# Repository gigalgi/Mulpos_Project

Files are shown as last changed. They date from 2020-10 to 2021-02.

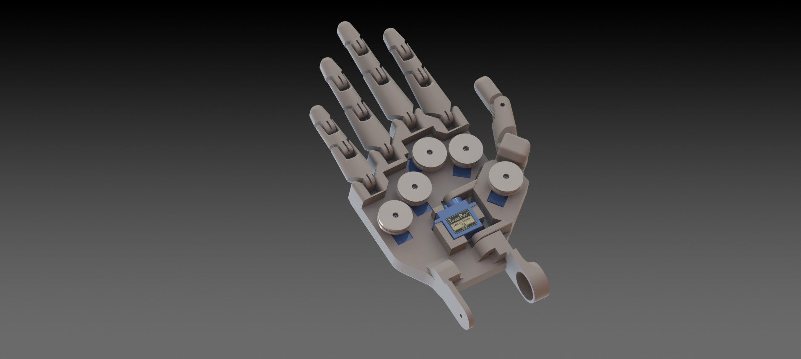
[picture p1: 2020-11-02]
MULPOS Piezas/Render/9.JPG

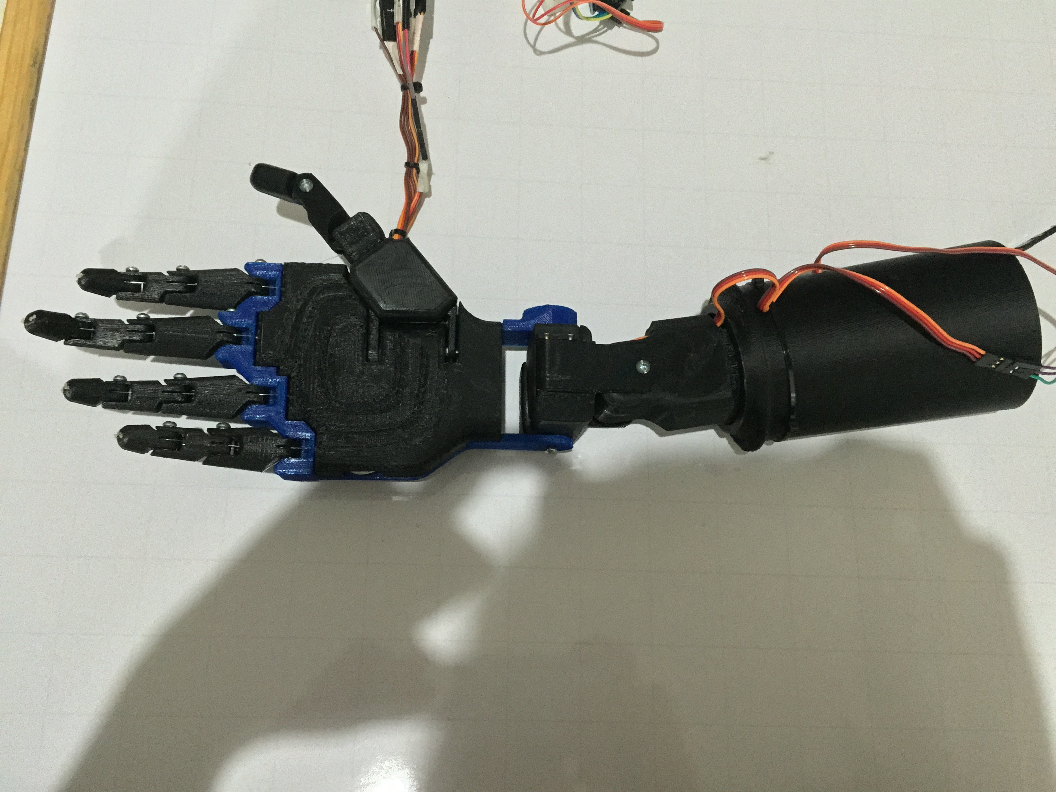
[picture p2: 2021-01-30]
STARPI/Render/IMG_1585.JPG

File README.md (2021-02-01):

# MULPOS Project

El objetivo del proyecto MULPOS es el diseño y desarrollo de sistemas protésicos caracterizados principalmente 
por su bajo costo y por su arquitectura open source, además de ofrecer alternativas funcionales a las prótesis 
tradicionales.

Para la reducción de costos de los sistemas a diseñar se proponen técnicas aditivas de construcción 
como la impresión 3D. La experiencia de controlar un miembro artificial de una manera intuitiva y similar a la de 
uno natural es prerrequisito del proyecto, por lo que se busca desarrollar interfaces basadas en bioseñales como 
son las que pueden ser obtenidas a través de los músculos o el cerebro.

Se busca a través de la reducción de costos permitir a la mayor parte de la población la mejora de la calidad de vida
con prótesis que emulen el miembro ausente tanto en aspectos de apariencia como funcionales.
El caracter open source del proyecto tiene como objetivo el facilitar la construcción de estos dispositivospor personas 
con conocimientos limitados de diseño CAD además de fomentar el interés por el desarrollo de destrezas en esta área.   

Para mas informacion visite nuestro sitio web www.moveorobotics.com o contactenos a traves de email: support@moveorobotics.com

##

The objective of the MULPOS project is the design and development of prosthetic systems characterized mainly by 
their low cost and open source architecture, in addition to offering functional alternatives to traditional prostheses.

To reduce the costs of the systems to be designed, additive construction techniques such as 3D printing are proposed. 
The experience of controlling an artificial limb in an intuitive way and similar to that of a natural one is a prerequisite
of the project, which is why it seeks to develop interfaces based on biosignals such as those that can be obtained through 
the muscles or the brain.
       
It is sought through cost reduction to allow the majority of the population to improve the quality of life
with prostheses that emulate the absent limb in both appearance and functional aspects.The open source 
nature of the project aims to facilitate the construction of these devices by people with limited knowledge
of CAD design, as well as to encourage interest in the development of skills in this area.

For more information visit our website www.moveorobotics.com or contact us via email: support@moveorobotics.com

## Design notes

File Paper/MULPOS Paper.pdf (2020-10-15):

# Diseño de una prótesis mioeléctrica de miembro superior de código abierto

Galvis Giraldo Gilberto

1

, García Arias Luis Felipe²

, Jaramillo Pineda Victor Alfonso³ gigalgi@hotmail.com¹

, feligar14@hotmail.com²

, victor.jaramillo@ucaldas.edu.co³ Department of Physics, Mechatronics Engineering Program, University of Caldas Manizales (Colombia)

Resumen__El propósito de este artículo fue desarrollar una prótesis capaz de emular la naturaleza y funcionamiento de una mano humana, de tal manera que el individuo que la use logre mejorar su calidad de vida sin tener que someterse a métodos invasivos que requieren otros tipos de procedimientos. La adquisición de las señales eléctricas que activan el movimiento de los músculos se logró por medio de un sistema de electromiografía superficial (ECG), con esto se identificaron los patrones de las señales obtenidas indicando las diferentes funciones de la mano y se tradujeron en movimientos mecánicos por medio de ocho servomotores integrados en el diseño de la prótesis. Para captar las señales eléctricas se implementó un electromiógrafo con cinco electrodos, para el procesamiento de la señales y la ejecución de los movimientos se optó por un microcontrolador Arduino, el diseño se realizó en un software de dibujo asistido por computadora (CAD) y finalmente aprovechando la tecnología de impresión 3d se puedo obtener el modelo físico de la prótesis teniendo como valor agregado su bajo puesto que el objetivo es que sea asequible para cualquier persona. Finalmente se logró un control eficiente y versátil similar a como se controla la mano del ser humano, para el bien y mejoramiento de la calidad de vida de las personas que no cuentan con grandes recursos económicos y carecen de esta extremidad.

Palabras claves: Arduino, bajo costo, código abierto electromiografía, electrodos, prótesis, servomotores, señales,

Abstract__ The purpose of this article was to develop a prosthesis capable of emulating the nature and functioning of a human hand, so that the individual who achieves use improve their quality of life without having to undergo invasive methods that require other types of procedures, the acquisition of the electrical signals that trigger muscle movement is achieved through electromyography (ECG) by placing electrodes on the skin, with patterns that the signals obtained were identified indicating the different functions of the hand translating into mechanical movements through integrated in the design of the prosthesis servomotors, a total of 8 servo motors is used to capture the electrical signals one electromyograph five electrodes was implemented, for the processing of signals and execution of movements chose a Arduino microcontroller, the design is performed in a software-aided drafting (CAD) and finally taking advantage of 3D printing technology will I get the physical model of the prosthesis having as value added his low since the goal is to make it affordable for Anyone. Finally an efficient and versatile control similar to the human hand, for good and improving the quality of life of people who do not have large financial resources and lack of this tip is controlled achieved.

Keyword: Arduino, low cost, open source, electromyography, electrodes, prosthesis, servomotors, signals

I. Introducción

La tendencia global hacia el uso de dispositivos wereables desafía al desarrollo de productos compactos y fáciles de usar, el diseño de las interfaces entre estos y el usuario constituye la parte clave del proceso. Así mismo, se presenta una tendencia en investigadores hacia el desarrollo de dispositivos e interfaces orientadas a usuarios que poseen algún tipo de limitación física o motora. Como ejemplos se puede encontrar en la literatura científica desarrollos que se basan en el reconocimiento del usuario como parte integral del sistema a través de técnicas de procesamiento de imágenes [2,7], otros enfoques se basan en la adquisición de bioseñales como son las obtenidas a través de dispositivos de electroencefalografía (EEG), electrooculografía (EOG) y electromiografía (EMG) [3, 4, 5, 6].

Entre los desarrollos mencionados se encuentran dispositivos protésicos que permitan a usuarios con algún grado de amputación, la realización de todo tipo de tareas de la manera más fiel posible a la que le permitiría una extremidad natural. Entre las características destacables de una buena prótesis de mano se encuentran: Versatilidad en la ejecución de gestos, integridad con el tiempo de la interfaz implementada, bajo costo, apariencia realista. Aunque existen en el mercado alternativas de vanguardia que posibilitan un amplio reconocimiento de gestos, constituyen opciones de alto costo, lo que imposibilita el acceso de una amplia gama de la población.

En este trabajo se propone el diseño de una prótesis de mano de código abierto, que pueda ser implementada a través de métodos aditivos de fabricación. Se busca obtener un dispositivo de bajo costo que pueda ser personalizado por un usuario con conocimientos básicos de CAD. Del mismo modo se propone un sistema de adquisición y procesamiento de señales EMG basado en una plataforma de código abierto.

II. | Marco Teórico

En la actualidad existen diferentes tipos de prótesis (ver tabla 1), algunas difíciles de utilizar, baja eficiencia y algunas demasiado costosas y de difícil acceso para la mayoría de las personas. Se pueden encontrar prótesis de miembro superior del tipo protésico, que solo realizan presión tridigital con oposición entre los dedos índice y medio con el pulgar, este tipo de prótesis pueden ser mecánicas o electromecánicas, son relativamente económicas y de fácil acceso. Existen también sistemas protésicos de tipo de gancho que realizan presión digital, ofreciendo funcionalidad limitada al usuario.

Tipo | Características Principales
Mecánica | Se usa con la función de cierre o apertura a voluntad. Solo puede ser utilizada para el agarre de objetos relativamente grandes y redondos, debido a la poca precisión del mecanismo.
Eléctrica | Utiliza motores eléctricos en los dispositivos terminales, muñeca y codo, con una batería recargable. Es posible controlarla de varias formas: servo control, botón pulsador o un interruptor con arnés.
Híbrida | Combina el movimiento del cuerpo con el accionamiento por electricidad. Este concepto es utilizado en la prótesis transhumerales, donde el codo es accionado por el cuerpo y el dispositivo terminal (gancho o mano) es de accionamiento mioeléctrico.

Tabla 1. Fuente: http://www.elhospital.com/temas/Colombia-avanza-en-el-desarrollo-de-protesis-mioelectricas+102438, consultada el día 28 de julio de 2015

La tecnología mioléctrica comenzó a implementarse en las prótesis de extremidad superior de tipo protésico a mediados del siglo XX [7]. La incorporación de sensores que captan la actividad electromiográfica (EMG) de los músculos remanentes del muñón y lo traducen en un movimiento de la mano protésica constituyo un gran salto en la calidad de las prótesis de extremidad superior [8]. Las manos mioeléctricas, los usuarios a menudo abandonan la prótesis mioeléctricas de antebrazo debido a los problemas de control y la ausencia de retroalimentación. Muchas de las investigaciones modernas se centran en el aumento de la funcionalidad de las nuevas prótesis, pero existen otro tipo de trabajos donde los más importante es la aceptación del usuario [9] y la adaptabilidad del usuario con la prótesis buscando así construir una prótesis que tenga gran similitud con la calidad de los movimientos a la de una mano humana.

Por otro lado existen desarrollos de prótesis de miembro superior cada vez más versátiles, que incorporan tecnología de vanguardia, como lo es el sistema creado por Touch Bionics llamado iLimb Ultra. La prótesis se ve y se mueve como una mano natural, tiene todos los dedos motorizados permitiendo emular movimientos naturales y además el usuario puede personalizarla para sus necesidades específicas [10]. Se presenta como un dispositivo funcional pero de difícil acceso con un costo que oscila alrededor de 100.000 dólares.

En nuestro trabajo proponemos una prótesis de miembro superior funcional, con movimientos independientes en cada uno de los dedos y que su costo de fabricación no supere los 150 dólares para permitir el acceso de cualquier usuario al dispositivo. Se propone la impresión 3D como forma de fabricación puesto que permite producir prototipos personalizados y resulta la mejor opción para construir una prótesis de bajo costo para personas de bajos recursos [11].

III. | Métodos y materiales

Para la construcción de la prótesis que se propone en este trabajo se tuvo en cuenta diferentes parámetros de diseño, entre ellos la adaptabilidad para el futuro usuario, el control electrónico y la eficiencia, todo teniendo que cuenta que debe ser una prótesis que se asemeje en sus movimientos a los de la mano humana, fácil de controlar y que su costo de fabricación sea inferior a 150 dólares. A continuación se detallan cada una de las etapas de diseño y construcción.

A. Estructura física de la mano y parámetros de diseño

El diseño y control de esta prótesis se basa en las características mecánicas, eléctricas y morfológicas de la mano, la muñeca y el antebrazo del ser humano. Se busca imitar características de apariencia y funcionalidades perfeccionadas durante miles de años de evolución.

Para el diseño de esta prótesis de mimbro superior se usó un software de diseño asistido por computadora (CAD), el cual permite realizar pruebas de resistencia y esfuerzo al igual que realizar múltiples modificaciones sin la necesidad de fabricar prototipos. En el diseño se consideraron tanto el aspecto físico como el funcionamiento mecánico, plasmando en el diseño un esqueleto que forma la estructura base. Esta estructura integra el tejido y los huesos ubicados en la palma y dorso de la mano, además de fusionar los múltiples huesos que componen la muñeca humana (ver figura 1). Se conservan las falanges proximal, media y distal como elementos independientes, unidas en la mano humana a través de articulaciones metacarpofalángicas e interfalángicas. Las articulaciones metacarpofalángicas son articulaciones condíleas que permiten: flexión, extensión, abducción, aducción, circunducción y una rotación limitada [12]. Las articulaciones interfalángicas de la mano son de tipo bisagra y permiten principalmente los movimientos de flexión y de extensión [12]. La ubicación de estas articulaciones se muestra en la figura 2.

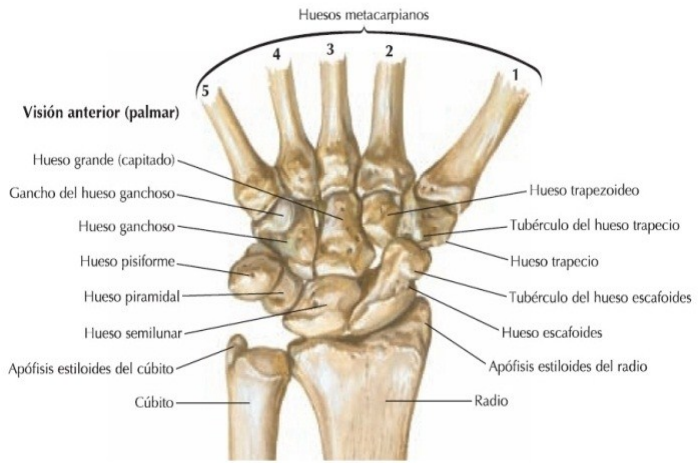
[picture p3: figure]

Figura 1.Huesos que componen la muñeca humana. Imagen tomada de Atlas de Anatomía Humana - Netter - 5ed p 440

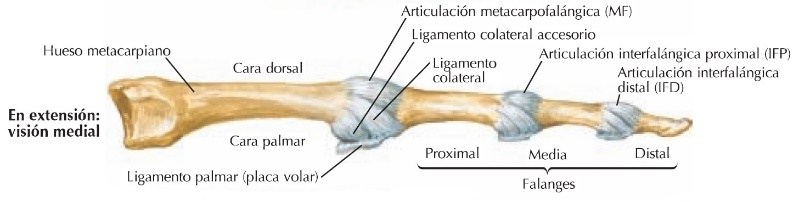
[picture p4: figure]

Figura 2. Ubicación de las articulaciones de un dedo de la mano humana

El material seleccionado para construir el prototipo fue el plástico ABS dada su resistencia, bajo peso y flexibilidad características que comparte con los huesos humanos, este material tiene como valor su bajo costo, maleabilidad y resistencia. Las articulaciones fueron incluidas en el diseño igualando su funcionamiento al acoplar las falanges como eslabones que rotan alrededor de un eje. Para lograr los movimientos mencionados de los dedos se emulo con servomotores el conjunto de músculos: flexor profundo y extensor de los dedos, que se encuentran en el antebrazo. El músculo flexor profundo produce el movimiento cuatro tendones que pasan por el túnel del carpo y se dirigen hacia los cuatro dedos mediales. Los tendones cruzan la muñeca, por lo que también puede flexionar dicha articulación [12]. El músculo extensor de los dedos es extensor de los cuatro dedos mediales (índice, medio, anular y meñique), cada tendón se inserta en la base de las superficies dorsales de las falanges media y distal [12].

Existe también otro musculo que es el flexor largo del pulgar que origina el movimiento a un único tendón alargado, pasa por el túnel del carpo, y hace que se flexione el pulgar [13]. Otro musculo que interfiere es el músculo extensor largo del pulgar, que extiende todas las articulaciones de este [12]. (Ver figura 3), también se tuvo en cuenta el musculo oponente del pulgar que rota y flexiona el primer metacarpiano sobre el trapecio, de manera que sitúa la yema del pulgar enfrentada a las de los otros dedos [12]. (Ver figura 4).

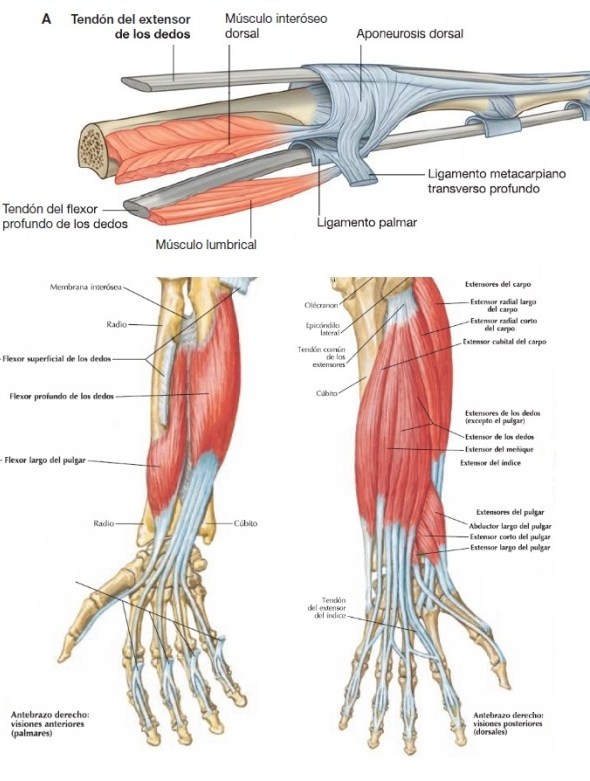
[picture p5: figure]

Figura 3. Musculo extensor largo del pulgar. Imagen tomada de Atlas de Anatomía Humana - Netter - 5ed. pp 429,431

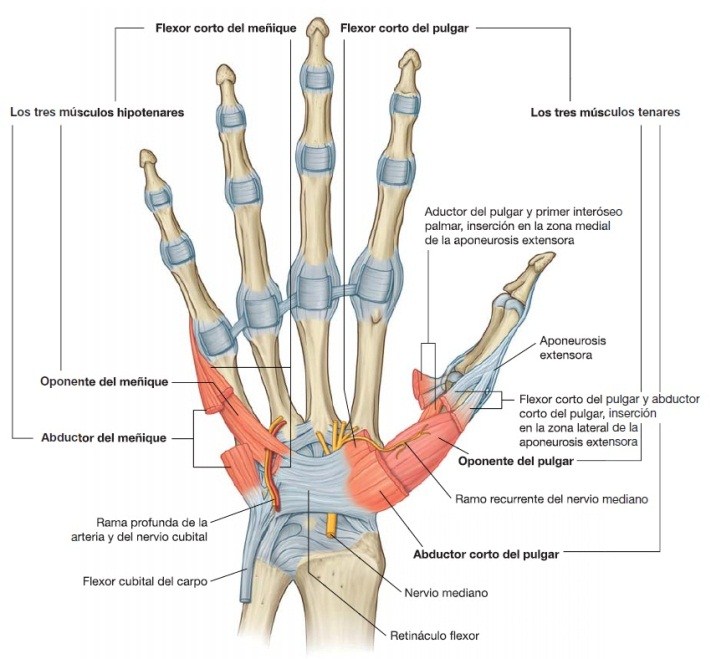
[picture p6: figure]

Figura 4. Mano humana con los músculos flexores. Imagen tomada de Gray anatomía para estudiantes 2ª ed. pag 765

El movimiento muscular mencionado se activa por neuronas motoras asociadas a cada músculo. Estas células nerviosas son comandadas a través de señales eléctricas que se originan en el cerebro y viajan a través de la médula espinal. Para determinar la posición en que se encuentra cada una de las partes del cuerpo se encuentra una estructura llamada huso neuromuscular que está conformado por neuronas sensitivas y motoras (Ver figura 5). Este tipo de estructuras se encuentra en las regiones tendinosas de los músculos y es más abundante en las regiones que deben ejecutar movimientos con destreza. [14]

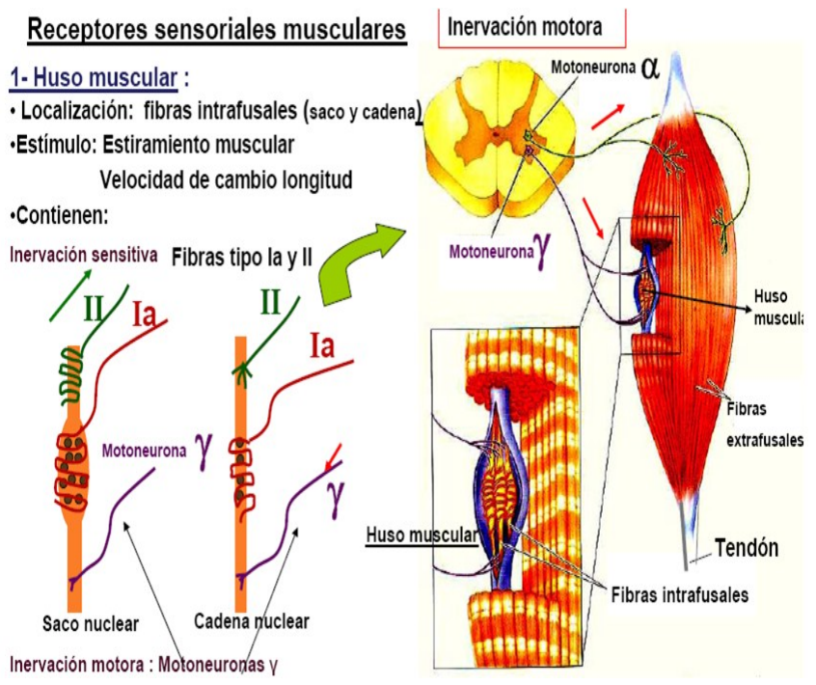
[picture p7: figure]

Figura 5. Huso muscular.
Imagen tomada de http://1.bp.blogspot.com

Para los tendones se seleccionó como material el nylon debido a su resistencia a la extensión y capacidad de flexionarse sin sufrir fatiga, las funciones de contracción y relajación de los músculos se producen con servomotores debido a su fácil manejo, gran cantidad de fuerza y tamaño reducido, siendo ideales para ser incorporados dentro de la estructura de la mano (ver figura 5), permitido realizar de manera muy precisa el cierre y apertura de la mano ya que se cuenta con un total de seis servomotores de los cuales dos de ellos son usados por el pulgar, uno para realizar la flexión y extensión del pulgar y el otro para realizar el movimiento de oposición del pulgar los cuatro servos restantes se dividen para los otro cuatro dedos, esto con el fin de otorgarle a la prótesis la misma libertar de apertura y cierre individual o conjunta de los de dedos para una mejor sujeción de los objetos, también se agregaron los movientes de la muñeca y el antebrazo que son los movimientos de pronación, supinación, flexión y extensión de la muñeca, para estos movimientos se involucran otros músculos [12] (ver figura 6).

Para reemplazar el papel de los tendones se seleccionó el Nylon debido a su capacidad de flexionarse y estirarse sin sufrir fatiga.
[22] Se seleccionan servomotores para realizar las funciones de contracción y relajación de los tendones, ejecutadas en el cuerpo por los músculos. Como criterio de diseño para la selección de los actuadores mencionados se establecieron características como el tamaño, torque y facilidad al momento de ser controlados. El Nylon se sujeta de la falange distal y pasa por las falanges media y proximal sobre las caras anterior y posterior de cada uno de los dedos formando dos tendones en cada uno. El material usado para reemplazar los tendones se conecta al actuador a través de una polea, cada una de las direcciones de giro del motor corresponde a una acción de contracción o relajación del músculo que a su vez se relaciona con la flexión o extensión del dedo. (Figura 7)

El sistema de movimiento de los componentes de la prótesis se compone de seis actuadores. Cada dedo posee un servomotor que permite los movimientos de flexión y extensión individual y en conjunto el cierre y apertura precisa de la prótesis. Se añade un actuador adicional en el dedo pulgar que le añade un movimiento de oposición y mejora la sujeción de objetos. Se agregó al sistema un mecanismo de 4 grados de libertad (DOF) a través de tres servomotores que permite los movimientos de pronación, supinación, flexión y extensión de la muñeca, desviación cubital y desviación radial (aducción y abducción).

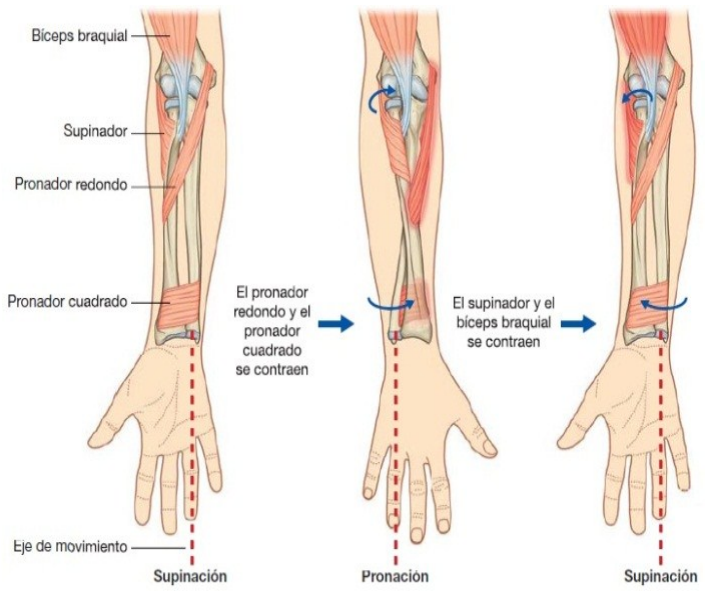
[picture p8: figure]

Figura 6. Músculos de supinación y pronación.
Imagen tomada de Gray anatomía para estudiantes 2ª ed. pag 736

El flexor cubital del carpo es el más medial de los músculos flexores del plano superficial, su función es la de flexionar y aducir la articulación de la muñeca, el músculo flexor radial del carpo se sitúa lateral al palmar largo, y tiene un tendón largo y prominente en la mitad distal del antebrazo [15]. El flexor radial del carpo es un potente flexor de la muñeca, y también puede abducir esta articulación (ver figura 6), El músculo extensor radial largo del carpo se origina en la zona distal de la cresta supracondílea y en el epicóndilo lateral del húmero el extensor radial largo del carpo extiende y abduce la muñeca, el músculo extensor cubital del carpo se sitúa medial al extensor del dedo meñique. Tiene su origen en el epicóndilo lateral, y su tendón se inserta en la cara medial de la base de V metacarpiano.

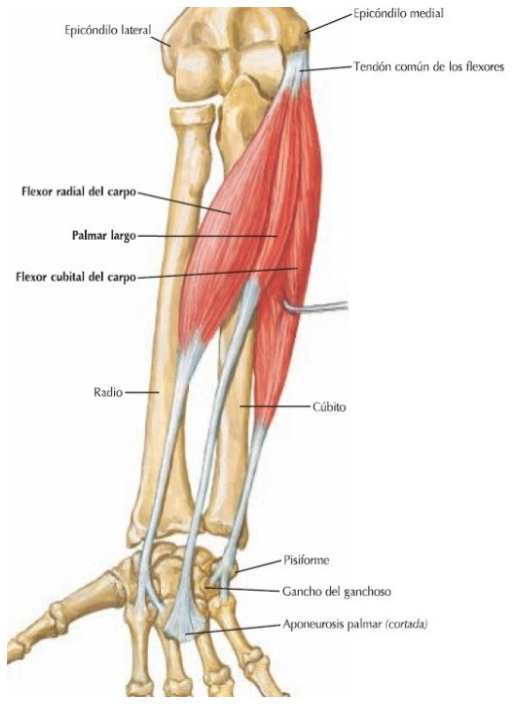
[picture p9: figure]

Figura 7. Músculo flexor radial del carpo, flexor cubital del carpo y palmar largo.
Imagen tomada de Atlas de Anatomía Humana - Netter – 5ª ed. pag 430

El extensor cubital del carpo extiende y aduce la muñeca [12] (ver figura 8), estos movimientos son implementados en el diseño mediante una unión con la muñeca utilizando un mecanismo que simula una junta universal por medio de dos servos con los cuales se logran los movimientos de flexión de la muñeca, extensión de la muñeca, desviación cubital y desviación radial (abducción y aducción), los movimientos de pronación y supinación se realizan con un último servo el cual al girar hacia un lado o hacia el otro imitando de igual manera que el mecanismo del cardan de forma muy precisa dichos movimientos utilizan así un total de 9 servo motores para lograr emulara con gran exactitud los movimientos más importantes de la mano humana.

Para el control de dicha prótesis se captan las señales eléctricas que activan el movimiento de los músculos, por medio de una electromiografía (EMG) colocando electrodos sobre la piel se identificaron patrones en la señales obtenidas que indicaran movimientos como la flexión, extensión, supinación, pronación, desviación cubital y desviación radial traduciéndolas en movimientos mecanismos por medio de los servos ya mencionados integrados en la prótesis asemejándose al sistema nerviosos pues el servo motor emula de igual manera las partes básicas empleadas para realizar el movimiento siendo su motor el musculo, su controlador las neuronas motoras y los huesos neuromusculares siendo quienes ejecutan la información recibida y envía nueva información sobre su longitud es decir que tan contraído esta y su posición. Para procesar estas señales se usó un microcontrolador Arduino siendo este quien da la orden final de que movimiento se debe realizar de igual manera que lo hace el cerebro al enviar la información en forma de pulsos eléctricos a través del sistema nervioso llegando a las neuronas motoras y huesos neuromusculares dispuestos en los músculos indicándole la instrucción que debe ejecutar el musculo realizando así el movimiento y tarea deseada.

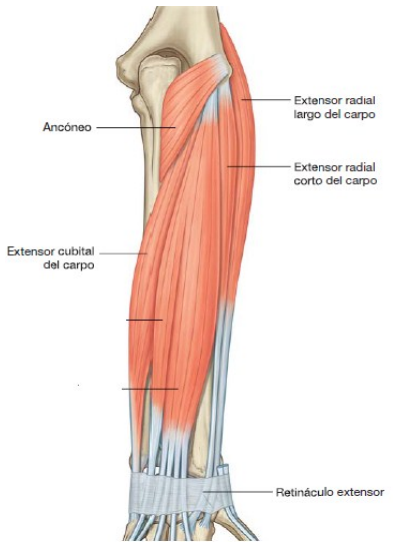
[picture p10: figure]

Figura 8.Músculo extensor cubital del carpo.
Imagen tomada de Gray anatomía para estudiantes 2ª ed. pag 746

Después del análisis anatómico de la mano humana que se realizó se procedió a diseñar un prototipo teniendo en cuenta todos los parámetros de movimiento (ver figura 9).

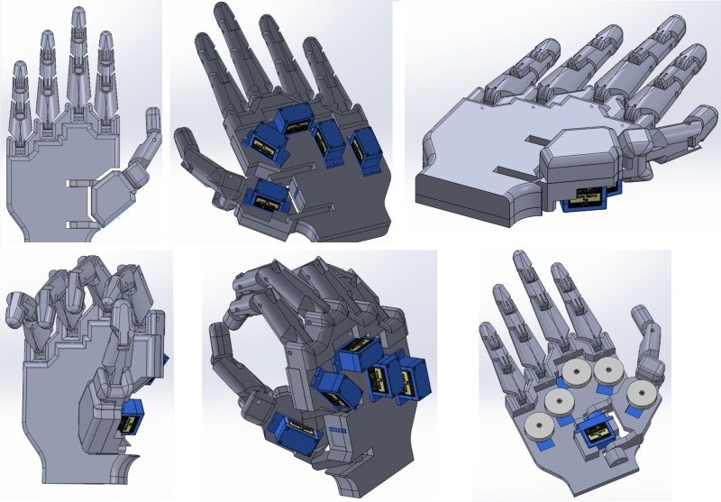
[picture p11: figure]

Figura 9. Diseño final de la prótesis de miembro superior.

B. Adquisición de señales EMG

Desde mediados del siglo 20 se ha abordado el uso de señales tomadas directamente desde los músculos como una manera de controlar diferentes tipos de dispositivos [16]. Esta tendencia ha aumentado recientemente a medida que mejoran los métodos de fabricación aditiva y las técnicas de adquisición y procesamiento
de | bioseñales. | La | posibilidad | de | obtener | señales
electromiográficas (EMG) desde la superficie de la piel de un miembro amputado se presenta como una forma intuitiva en la que el usuario puede comandar prótesis activando las unidades motoras residuales del miembro objetivo [17,18]. Para el control intuitivo de una prótesis como la que se presenta en este estudio se presentan a continuación consideraciones en el diseño de un sistema de adquisición de señales EMG y en el modo con que estas son procesadas.

Sistema de Electromiografía

En la figura se muestra el diagrama de bloques de un sistema para la adquisición de señales EMG. El sistema se compone de una etapa de adquisición y pre amplificación de la señal, una etapa de filtrado y amplificación posterior. Para el dispositivo a desarrollar se incluye en el esquema una etapa de acondicionamiento que permita ajustar los valores de tensión de la señal para que esta pueda ser procesada por un microcontrolador. La amplitud de la bioseñal objetivo ronda los 10 mV [19], por lo que se selecciona una ganancia del sistema de 1200. Se establece una ganancia de 40 para la etapa de preamplificación y una de 30 para la etapa de amplificación. La etapa de filtrado se compone por un filtro pasa altas y uno pasa bajas, cuyas frecuencias de corte se establecen en 70 Hz para el filtro pasa altas y 500 Hz para el filtro pasa bajas, típicamente esta primera se establece entre los 10 y los 20 Hz. Las frecuencias más bajas en el espectro de la señal corresponden a los mecanismos de disparo de los músculos motores y no contribuyen significativamente al sistema de reconocimiento de gestos [20,21]. De este modo Li et al [21] establecen en su investigación una frecuencia de corte de 60 Hz para mejorar el rechazo del sistema a señales características de la red eléctrica europea (50 Hz) y así mismo se selecciona una frecuencia de corte de 70 Hz para el dispositivo desarrollado en este trabajo por el entorno en que será usado

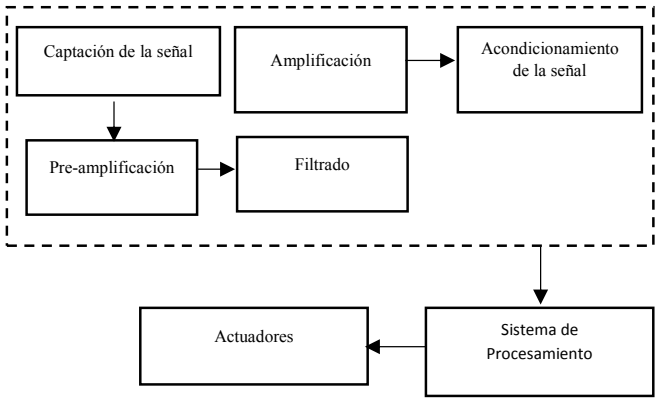
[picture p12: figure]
Captación de la señal; Pre-amplificación; Filtrado; Amplificación; Acondicionamiento; de la señal; Sistema de Procesamiento; Actuadores

Diagrama de bloques del sistema de adquisición y posicionamiento.

Se diseñó un circuito electrónico para el electromiógrafo con un amplificador de instrumentación de referencia INA126, debido a las características de rechazo de modo común, bajo voltaje de offset y a su bajo costo, en la figura 10 se muestra el diagrama del circuito.

IV. Resultados

Primero se diseñó y se construyó un prototipo en madera (ver figura 11) que funcionaba con comandos de voz y con una aplicación para dispositivo móvil [23], utilizando los sensores del teléfono (acelerómetro y giroscopio) este prototipo inicial sirvió para analizar los movimientos, obtener datos de diseño y de eficiencia, ya con todos los datos necesarios se procedió a diseñar una prótesis más eficiente como la que se mostró en este trabajo.

En el primer prototipo de la prótesis la forma de oposición de pulgar se realizaba de manera que el pulgar rotara sobre sí mismo, manteniendo su posición con respecto a la palma, pero variando su dirección rotando desde una posición en la que se mantenía paralelo a los demás dedos hasta una posición en la que el pulgar podía flexionarse hacia adentro de la palma realizando la oposición, pero dado que el pulgar se mantenía en el mismo lugar al rotar le impedía a la prótesis una buena sujeción, por estos motivos se decido modificar este sistema de forma que el pulgar se opone para mejorar el agarre al sujetar cualquier tipo de objeto esta nueva forma hace rotar el dedo hacia la palma de la misma manera en la que se opone el pulgar de la mano del humano realizando un movimiento más natural acorde con la bilogía humana, otorgando mayor funcionalidad, además este nuevo prototipo puede tocar todos los dedos desde la punta hasta la base proporcionando una mejor eficiencia para la sujeción de objetos pequeños.

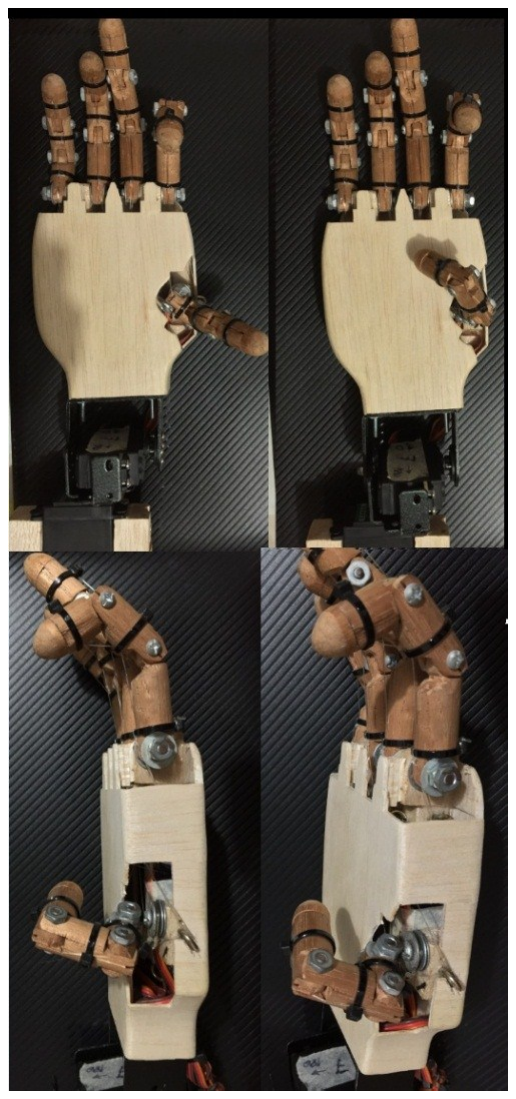
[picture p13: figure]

Figura 11. Diseño inicial en madera de la prótesis.

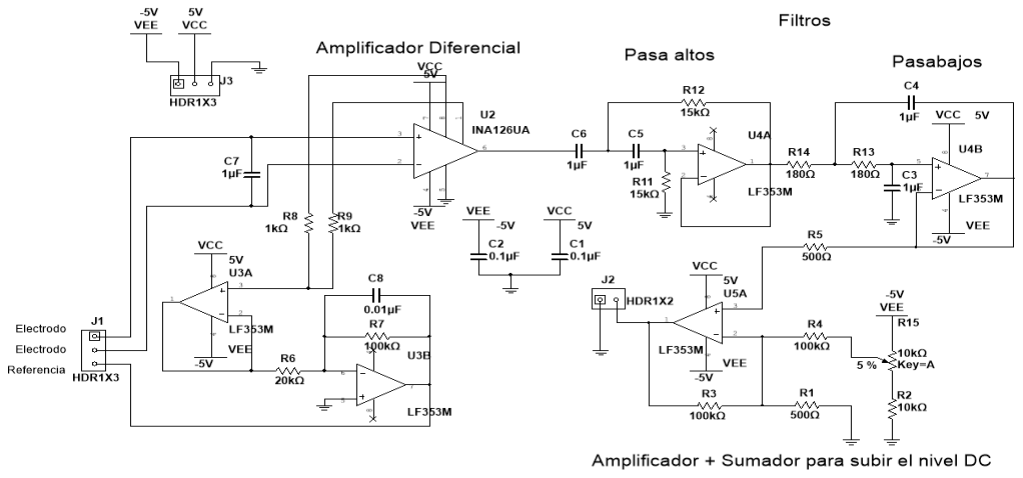
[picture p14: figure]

Figura 10. Diagrama esquemático del electromiógrafo.

V. Conclusiones

Se obtuvo una prótesis de miembro superior con un costo de fabricación inferior a los 150 dólares lo que hace que sea accesible para casi cualquier persona que tenga ausencia de un miembro superior.

Cambiando el diseño mecánico del dedo pulgar se obtiene un aumento considerable de la funcionalidad de la prótesis, lo que se pudo verificar comparando las dos prótesis construidas.

REFERENCIAS

[1] M. Al-Rousan, K. Assaleh, A wavelet- and neural network-based voice systemfor a smart wheelchair control, J. Frankl. Inst.-Eng. Appl. Math. 348 (1) (2011)90–100,
[2] X. Shen, G Hua, L. Williams, Y. Wu, Dynamic hand gesture recognition: An exemplar-based approach from motiondivergence fields, Image and Vision Computing 30 (2012) 227–235.
[3] D. Purwanto, R. Mardiyanto, K. Arai, Electric wheelchair
control | with gazedirection | and | eye | blinking, | in:
Proceedings of the 14th International Sympo-sium on Artificial Life and Robotics, AROB, Oita, Japan, February 5–7, 2009,pp. 400–436
[4] J.Y. Long, Y. Li, H. Wang, T. Yu, J. Pan, F. Li, A hybrid brain com-puter interface to control the direction and speed of a simulated or realwheelchair, IEEE Trans. Neural Syst. Rehabil. Eng. 20 (5) (2012) 720–729
[5] R. Barea, L. Boquete, M. Mazo, E. Lopez, L.M. Bergasa, EOG guidance of awheelchair using neural networks, in: 15th International Conference onPattern Recognition, ICPR, vol. 4, Barcelona, Spain, 2000, pp. 668–671,
[6] A. Phinyomark, C. Limsakul, A review of control methods for elec-tric power wheelchairs based on electromyography signals with specialemphasis on pattern recognition, IETE Tech. Rev. 28 (4) (2011) 316–326.
[7] Zecca M., Micera S., Carroza M., Dario P., “Control Of Multifunctional Prosthetic Hands By Processing The
Electromyographic | Signal”, | Critical | Reviews™ | in
Biomedical Engineering. Vol. 30, pp. 459 485.2002.
[8] Garcia, D., Espinoza, M., J., «Avances en prótesis: una mirada al presente y al futuro,» Revista Médica Clínica Las Condes, vol. 25, nº 2, pp. 281-285, 2014.
[9] T. Bionics, «Touch Bionics,» 2015. [En línea]. Available: http://www.touchbionics.com/products/active-prostheses/ilimb-ultra. [Último acceso: 21 07 2015].
[10] B. Peerderman, «Myoelectric forearm prostheses: State of the art from a user-centered perspective,» Journal of rehabilitation research and development, vol. 48, nº 6, pp. 719-738, 2011.
[11] Loera Perez., E., A., «Proyecto E-Nable Sobre El Desarrollo De Prótesis Mecánicas,» Universidad Autonama de Nuevo Leon.
[12] Richard L. Drake, A. Wayne Vogl, Adam W. Mitchell. Anatomía para estudiantes, Barcelona: Elsevier, 2010.
[13] Schunke, | Shulte, | Shumacher, | Voll, | Wesker.,
PROMETHEUS Texto y Atlas de Anatomía, Panaericana, 2005.
[14] John a. Kiernan, lippincott., W., wilkins.,W., Kluwer., H., El sistema nervioso humano: Una perspectiva anatómica, Barcelona: Lippincott Williams and Wilkins. Wolters Kluwer Health, 2009.
[15] Zecca M., Micera S., Carroza M., Dario P, «Control Of Multifunctional Prosthetic Hands By Processing The
Electromyographic | Signal,» | Critical | Reviews™ | in
Biomedical Engineering, vol. 30, pp. 459-485, 2002.
[16] Ajiboye. A. B., Weir. R. F., «A heuristic fuzzy logic approach to EMG pattern recog-nition for multifunctional prosthesis control,» IEEE Trans. Neural Syst. Rehabil.Eng, vol. 13, nº 3, p. 280–291, 2005.
[17] F.V.G. Tenore, A. Ramos, A. Fahmy, S. Acharya, R. etienne-Cummings,N.V. Thakor, «Decoding of individuated finger movements using surfaceelectromyography,» IEEE Trans. Biomed. Eng, vol. 56, nº 5, p. 1427–1434, 2009.
[18] L.J. Hargrove, G. Li, K. Englehart, B. Hudgins, «Principal
components | analysispreprocessing | for | improved
classification | accuracies | in | pattern-recognition-based
myoelectric control,» IEEE Trans. Biomed. Eng, vol. 56, nº 5, p. 1407–1414, 2009.
[19] Maria Hakonena, Harri Piitulainenb, Arto Visalaa, «Current state of digital signal processing in myoelectric interfaces and related applications,» Biomedical Signal Processing and Control, pp. 334-359, 2015.
[20] D.F. Stegeman, H.J. Hermens, «Standards for surface electromyography,» in:The European Project Surface EMG for Non-Invasive Assessment of Muscles(SENIAM), 2007.
[21] G. Li, Y. Li, L. Yu, Y. Geng, « Conditioning and sampling issues of EMG signals in motion recognition of multifunctional myoelectric prostheses,» Ann. Biomed. Eng, vol. 39, nº 6, p. 1779–1787, 2011.
[22] A. Carrera, «Elasticidad y dureza de los huesos», Universidad Tecnológica de Equinoccial, Escuela de Odontologia, 2013.

[23] Jaramillo Pineda, V. A., Pineda, J., & Garcia Arias, L.F., «Design of an automatic voice controlled system and remote control», IEEE Explora, pp. 1-5, 2014.

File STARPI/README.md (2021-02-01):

# STARPI

El proyecto STARPI nace a partir del proyecto MULPOS y el aprovechamiento de sus características para solucionar problemas en otros sectores en los que es necesario la presencia de la mano humana en algunas aplicaciones de alto riesgo, por este mismo motivo es aun mas riesgoso exponer una vida humana a algunas de estas actividades como: inspección en plantas radioactivas, inspección en lugares de presencia de gases (tóxicos o inflamables), inspección de expertos en aplicaciones especificas, control en desminado y desarmado de bombas.

Estas aplicaciones tienen algo en común, ya se evidencian antecedentes de robots de inspección o manipulación,muchos de estos con pinzas para sujeción o transporte de elementos la idea principal del proyecto es aprovechar estos robot para hacer un híbrido entre la mano humana y los robots como elementos de transporte y virtualización. Se emplean diferentes tecnologías para monitoreo y manipulación utilizando la visión artificial como control del STARPI.

Para mas informacion visite nuestro sitio web www.moveorobotics.com o contactenos a traves de email: support@moveorobotics.com

##

The STARPI project was born from the MULPOS project and the use of its characteristics to solve problems in other sectors in which the presence of the human hand is necessary in some high-risk applications, for this same reason it is even more risky to expose human lifes to some of these activities such as: inspection in radioactive plants, inspection in places of presence of gases (toxic or flammable), inspection of experts in specific applications, control in demining and dismantling of bombs.

These applications have something in common, there is already evidence of a history of inspection or handling robots, many of these with clamps for holding or transporting elements.The main idea of the project is to take advantage of these robots to make a hybrid between the human hand and robots such as elements of transport and virtualization. Different technologies are used for monitoring and manipulation using mainly artificial vision to control STARPI. 

For more information visit our website www.moveorobotics.com or contact us via email: support@moveorobotics.com

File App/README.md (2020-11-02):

# app android para el control de MULPOS
* Aqui encontraras el .apk para instalar el app de control para MULPOS si desea puedes modificarla el proyceto fue desarrollado con appinveror2.
Junto al apk esta el .aia que puede abrir y editar en la plataforma appinventor2 y construir una nueva app.
* http://ai2.appinventor.mit.edu/
##
Para mas informacion visite nuestro sitio web www.moveorobotics.com o contactenos a traves email: support@moveorobotics.com

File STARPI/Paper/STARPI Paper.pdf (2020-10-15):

Abstract— the world of robotics is becoming wider day, we can see how from decades ago robots provide aid and reduce risks to humans, based on mixed reality and the anatomy of the human hand a robotic hand that simulates create a lot of human movements. Also the system fully complies with the goals establecidad presenting a smooth functioning of artificial vision systems and mechanical design of the hand.

Index Terms— PID, Opencv, control system, real time, vision system, mixed reality, HSV filter.

I. INTRODUCCIÓN
L uso de la robótica en situaciones de operaciones precisas y manipulación de objetos a distancia, es cada vez más frecuente, y nos permite disminuir la intervención humana directa para evitar accidentes. De otro lado, vemos como el internet nos es cada vez más útil en el logro de la integración, visualización y manipulación remota de objetos, archivos e imágenes, con lo que se mejora también en el caso de la robótica, el control y el análisis de las operaciones. Considerando que en la actualidad los robots de inspección y manipulación de objetos en actividades remotas, tienen como manipulador principal una pinza con movilidad limitada, se ha desarrollado un proyecto que busca remplazar esta pinza por una mano con movimientos complejos similares a los obtenidos por la mano humana.
El proyecto consta de un sistema de realidad mixta [25], el cual genera mayor inmersión del operador, permitiéndole más comodidad al momento de manipular objetos y sentir profundidad por medio de esta; su principal innovación es la mano capaz de manipular una mayor cantidad de objetos y de realizar movimientos más complejos [30] que la pinza. La mano consta de movimiento independiente en cada uno de los cinco dedos, puede realizar diferentes movimientos como: Pronación, supinación, flexión, extensión, aducción y abducción de la muñeca; mientras que con los dedos puede realizar flexión, extensión, oposición del pulgar y reposición del mismo [28].

II. PROBLEMÁTICA
Los explosivos, la radioactividad, los gases tóxicos, las altas temperaturas, los riesgos eléctricos, entre otros, generan problemas de seguridad para las personas, y su solución representa un área de investigación amplia y un reto en diferentes áreas de las ciencias exactas e ingenierías en la búsqueda de como operar estos elementos de manera más segura, más eficiente y más rápida sin necesidad de la intervención humana.
Podemos observar como el mando a distancia de los robots similares a este tienen una baja eficiencia y un alto costo. Aunque los procesos se han estandarizado y mejorado a lo largo de los años, no ha habido un cambio sustancial desde la segunda guerra mundial, siendo bastante notorio el modo en el que el usuario controla los robots desde hace décadas con mandos y botonería algo poco práctico que genera confusión.
Por otra parte, es en la inspección en campo, donde los robots más se han adaptado, permitiendo una detección temprana y ayuda en algunos tipos de manipulaciones, pero sin ser totalmente autónomos aún en todas las tareas, ya que dejan brechas que deben ser solucionadas por equipo humano.
Se evidencia pues la necesidad de mayor movilidad mecánica de los actuadores, derivada de las limitaciones que tienen las pinzas actuales. Conociendo esto, se presenta una solución que puede ser aplicada a sistemas ya existentes, mejorando dos aspectos esenciales: el control del elemento de sujeción y la visualización del entorno.
| III. CONTROL

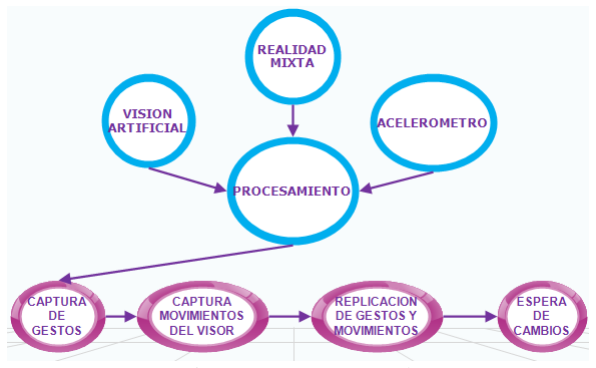
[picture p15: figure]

El funcionamiento de la propuesta planteada es llevar a cabo el funcionamiento como una unidad en conjunto logrando de esta forma que la persona que manipula esté a gusto y logre una

# Sistema de Tele-presencia Adaptable a Robots de Pinza para Inspección

Gilberto Galvis Giraldo
Universidad de Caldas
gigalgi@hotmail.com

Mateo Villegas Estrada
Universidad de Caldas
mateovi95@gmail.com

E

Fig. 1. Proceso general.

mejor experiencia y pueda lograr mejores resultados; funciona en dos planos inicialmente, primero se procesan los datos de los
movimientos | gestuales | posteriormente, | se | procesa | el
movimiento de realidad mixta para lograr reconocer las manipulaciones realizadas.

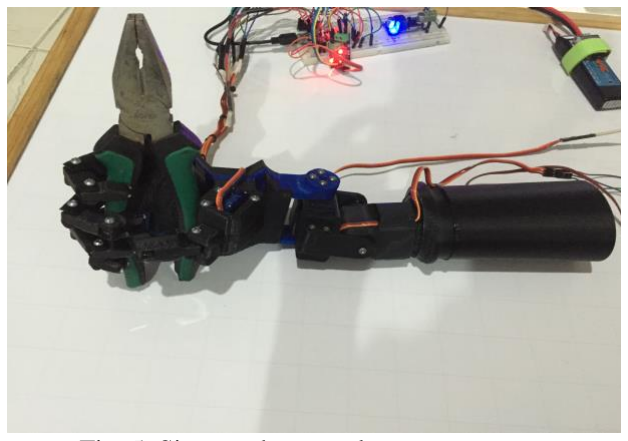
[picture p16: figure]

A. Sistema de visión artificial
Se realiza la captura y sensado de la mano humana por medio de una cámara de media resolución; se aplica un filtro HSV y un umbral para capturar la mano de una manera precisa; estos datos son exportados para posteriormente realizar un control de los dedos a accionar y la cantidad de presión que se debe ejercer en cada uno de ellos.
B. Sistema de control
El método de control del sistema consta de tres pasos: -Captura de datos.
-Procesamiento de datos.
-Control de la planta.

Se realiza un control PID discreto de aproximación rectangular; para solo calcular el incremento de la variable de control, utilizando como variable del proceso la corriente que consumen los motores, se realiza la realimentación de corriente para lograr el agarre mediante el uso de sistemas embebidos se calcula los parámetros variables en el PID, al obtener los datos provistos por el sistema de visión, ajustando los dedos en la posición correcta, generando ahorro de energía y de potencia; además produce menor desgaste en los motores y menor calentamiento de los mismos.[1]

C. Cámara
D. Realidad mixta

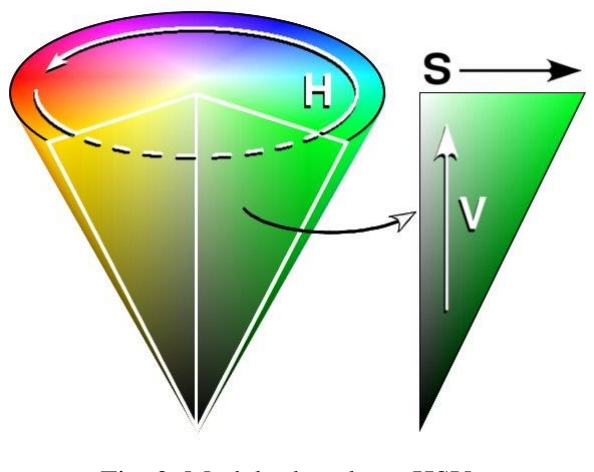
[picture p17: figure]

Fig. 2. Modelo de colores HSV.

TABLA I
LOGITECH C270
USB 2.0 High Speed | CMOS sensor
1280*720 HDR | UP to 30 fps
16:9 Screen Output | DC 5V/500mA

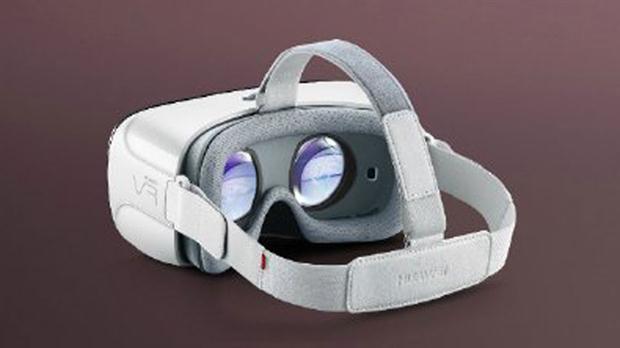
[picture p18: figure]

Fig. 6. Visor de realidad virtual.[47]

Fig. 5. Sistema de control mano y muñeca

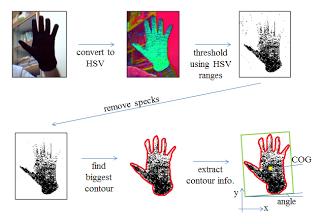
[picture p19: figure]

Fig. 3. Captura de datos. [46]

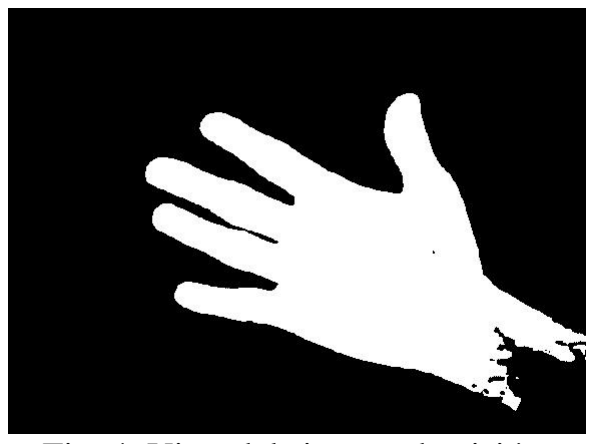
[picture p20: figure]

Fig. 4. Vista del sistema de visión.

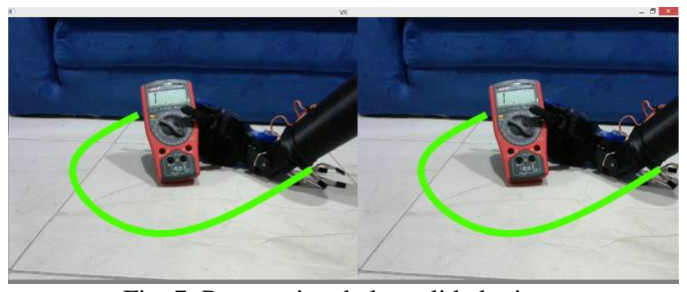
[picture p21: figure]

Realidad mixta, MR (Mixed Reality) o realidad híbrida es la unión entre el mundo real y el mundo virtual en tiempo real; esta realidad permite tener un espacio de interacción virtual con objetos del mundo real, además de la interacción con personas. La realidad mixta permite además de captar la profundidad, realizar la integración del movimiento de la cámara que se le adapta al robot con los movimientos del operario.

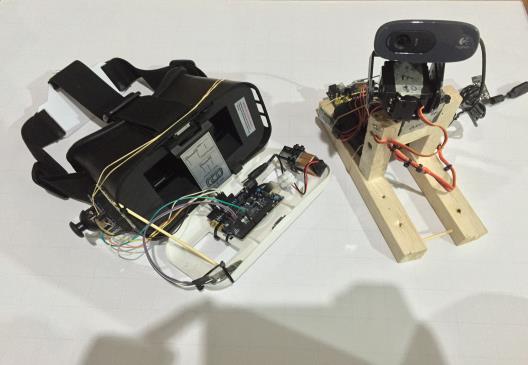
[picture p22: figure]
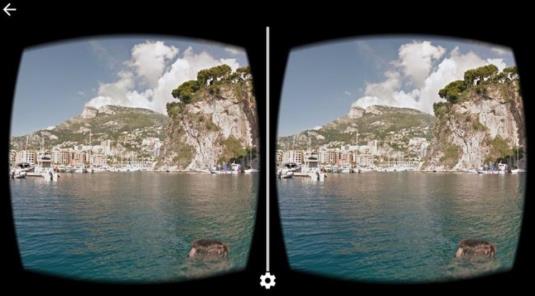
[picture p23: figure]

E. Sistema de inspección remota video streaming
Se implementó un sistema de inspección remota por medio de video en streaming para la monitorización en tiempo real del entorno en el que se encuentra trabajando el sistema para brindar un mayor soporte al operador en situaciones en las que se requiera de personal altamente calificado y este se encuentre en otro lugar del mundo.

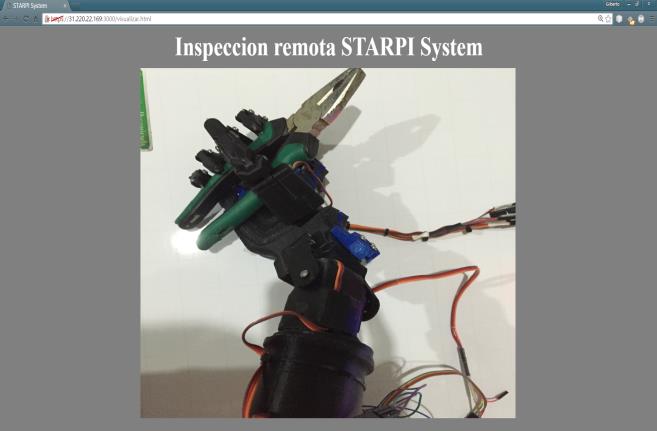
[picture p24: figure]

F. Control de la muñeca

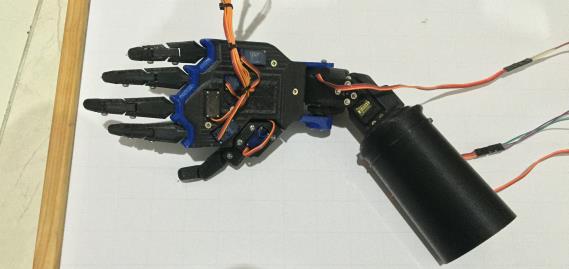
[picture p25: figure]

El control de la muñeca es realizado por un acelerómetro que se acopla a la mano humana para replicar el movimiento en la mano robótica, la que nos permite los movimientos de: Pronación, supinación, flexión, extensión, aducción y abducción, sin limitantes en cuanto a la movilidad en la misma.

Es de conocimiento del lector los efectos de aceleración explicados por la ley de la gravedad este es el principio del acelerómetro calculando el cambio del ángulo con las siguientes formulas, dado que el eje z es colineal a la fuerza de la gravedad es imposible determinar el cambio con el dispositivo utilizado.[49]
θy = atan

x
√y
2 + z

2

, θx = atan

y
√x
2 + z

2

Fig. 9. Vista de la realidad mixta.[48]

Fig. 10. Sistema inspección remota video streaming

Fig. 11. Sistema control de muñeca

Fig. 8. Sistema realidad mixta

Fig. 7. Perspectiva de la realidad mixta.

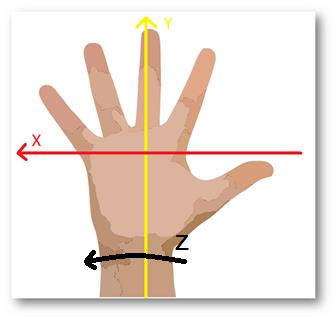
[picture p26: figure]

Fig. 12. Ejes acelerómetro.


G. Construcción de la mano


El diseño y control de esta mano robótica se basó en un trabajo previo que contemplaba las características mecánicas y morfológicas de la mano y la muñeca del ser humano. Se busca
imitar | características | de | apariencia | y | funcionalidad
perfeccionada durante miles de años de evolución.
Para el diseño de esta se usó un software de diseño asistido por computadora (CAD), el cual permite realizar pruebas de resistencia y esfuerzo, al igual que realizar múltiples modificaciones sin necesidad de fabricar prototipos. En el diseño se consideraron tanto el aspecto físico como el funcionamiento mecánico, plasmando un esqueleto que forma la estructura base. Esta estructura integra el tejido y los huesos ubicados en el interior de la mano, además de fusionar los múltiples huesos que componen la muñeca. Se conservan las
falanges | proximal, | media | y distal | como | elementos
independientes, unidas en la mano humana a través de articulaciones metacarpofalángicas e interfalángicas. Las
articulaciones | metacarpofalángicas | son | articulaciones
condíleas que permiten: flexión, extensión, abducción, aducción, circunducción y una rotación limitada [45]. Las articulaciones interfalángicas de la mano son de tipo bisagra y permiten principalmente los movimientos de flexión y de extensión. Después del análisis anatómico de la mano humana que se realizó se procedió a diseñar un prototipo teniendo en cuenta todos los parámetros de movimiento excepto separación de los dedos.[38][43]

IV. RESULTADOS

La respuesta obtenida por el sistema supero las expectativas, al lograr un muy buen comportamiento en movilidad y agarre con alta sujeción, al realizar pruebas de sujeción sometido a vibración de diferentes figuras geométricas se comprueba la capacidad de agarre de la misma; por otro lado, la inmersión en el mundo virtual genera una amplia visión del mundo real sin estar en el mismo. El sistema de visión genera una respuesta de alta precisión a los movimientos en la mano del operario.

Es de gran importancia generar mejor control y mayor facilidad en los diferentes entornos de aplicación del proyecto. Pero su integración con sistemas existentes permite un ahorro tanto económico como de tiempo de producción y pruebas.

V. ANÁLISIS DE RESULTADOS
El control realizado en la muñeca fue el adecuado, haciéndola totalmente funcional, superando los movimientos de la muñeca humana en algunos de los casos; además el sistema de visión funciona con gran precisión aunque se deben realizar algunas mejoras como se puede ver en la [figura 7].

Aparte de esto, se puede pensar en diferentes métodos de control más precisos [figura 14], pero la versatilidad del sistema de visión es bastante importante y no debe dejarse de lado, el control de visión es eficaz permitiendo realizar visión total del entorno y su fácil sistema de acoplamiento reduce el tiempo de operación.

VI. CONCLUSIONES
Se plantea una solución de bajo costo, factible al momento de implementación, que además puede ser reparado incluso de manera rápida de ser necesario; el correcto funcionamiento del sistema de visión requiere de una serie de factores de

Fig. 14. Mejora sistema de visión.[46]

Fig. 13. Diseño final mano y muñeca

Fig. 13. Acelerómetro adaptado.

iluminación y fondo estático, lo cual es un factor a corregir; por lo demás es un sistema viable y de buen funcionamiento.

REFERENCIAS
[1] K. Ogata, Modern Control Engineering, 5th Edition, Prentice Hall, 2009.
[2] Caio Felipe Favaretto, Henrique Corrêa Ramiro, Rômulo de Oliveira Souza e Marcelo Barboza Silva. Controle de um sistema Bola-Barra com realimentação através de imagen 2013.
[3] Hjelte Ulmehag, R., Hofwimmer, R., Klintberg, A., Skog Lidander, D., & Staberg, P. Ball and beam. 2012.
[4] Obando Correa, O. A., & Romero Brand, H. Desarrollo de un sistema ball and beam, para implementar estrategias de control mediante Labview.
[5] Gonzalez,R. & Woods,R. Digital image processing. Prentice Hall.2008
[6] W. Bolton, Mechatronics: Electronic control systems in mechanical and electrical engineering, 4th Edition, Prentice Hall, 2009.

[7]Hauser, J.,S.Sastry, and P. Kokotovic. “Nonlinear Control via Approximate Input-output Linearization: the Ball and Beam
Example”,IEEE | Transactions | on | Automatic | Control,
vol.37,no.3, IEEE,Piscataway, NJ,1992,pp.392-398.
[8] Barranco,A. | & Medel,J . Artificial | vision and
identification | for | intelligent | orientation | using | a
compass.Revista Facultad de Ingeniería de la Universidad de Antioquía, Vol. 58, pp. 191–198 2011.
[9] Handa,A.,Newcombe,R.A.,Angeli,A., & Davison,A.J.Real-time camera tracking: When is high framerate best?Lecture Notes in Computer Science,Vol. 7578, pp. 222–235.DOI: 10.1007/978-3-642-33786-4_17 2012.
[10] X. Fan, N. Zhang and S. Teng, Trajectory planning and tracking of ball and plate system using hierarchical fuzzy control scheme, Fuzzy Sets and Systems, vol.14, no.2, pp.297-312, 2003.
[11] Sossa,H. Features | for | object | recognition.Instituto
Politécnico Nacional.2006.

[12]Hartley,R. & Zisserman,A..Multiple view geometry in computer vision.CambridgeUniversity press,pp. 152–208. 2003.

[13] Tipsuwanpom, Runghimmawn, T Runghim, T. Intajag, and
S. Krongratana "Fuzzy logic PID controller based on FPGA for
process | control," | Industrial | Electronics, | 2004 | IEEE
International Symposium, Vol.2, No.11, 2004, 1495- 1500
[14] Basilio, J.C, Matos, S.R. Design of PI and PID
controllers with | transient | performance specification. In:
Education, IEEE transaction, Nov 2002, Volume 45, Issue 4, pp. 364-370 2002.
[15] Korrapati R.; Anderson, J.A; Swain, N.K; Swain M; “System Modeling Using Virtual Instruments” Southeast Con,
2002.Proceedings | IEEE | Digital | Object
Identifier:10.1109/.2002.995570 Publication Year: 2002, Page(s): 121 – 126.
[16] D'Souza, A., Advanced Dynamics: Modeling and Analysis, Prentice Hall (1984). Hamed, B.,“Application of Labview for Real-time Control of Ball and Beam System”, IACSIT Journal of Engineering and Technology, Vol.2, No.4 2010.
[17] Keeling, Christopher J. Modeling a Ball and Beam System Driven by an Electric Motor. 2010.
[18] K. C. Ng and M. M. Trivedi, Neural integrated fuzzy controller and real-time implementation of a ball balancing beam, Proc. of the 1996 IEEE Conf. on Robotics and Automation, Minneapolis, MN, U.S.A., pp.1590-1595, 1996.
[19] X. Doug and Z. Zhang, Applying genetic algorithm to on-line updated PID neural network controllers for ball and plate system, The 4th International Conference on Innovative Computing, information and Control, Kaohsiung, Taiwan, pp.751-755, 2009.
[20] G. Wang and Z. S. Sun, Algorithmic research on PD direct fuzzy control based on ball and plate apparatus, Electric Drive, vol.4, pp.23-25, 2004.
[21] P. Ponce, Inteligencia artificial con aplicaciones a la ingenieria, 1th edition, 2011.
[22] M. Al-Rousan, K. Assaleh, A wavelet- and neural network-based voice systemfor a smart wheelchair control, J. Frankl. Inst.-Eng. Appl. Math. 348 (1) (2011)90–100,
[23] X. Shen, G Hua, L. Williams, Y. Wu, Dynamic hand gesture recognition: An exemplar-based approach from motiondivergence fields, Image and Vision Computing 30 (2012) 227–235.
[24] D. Purwanto, R. Mardiyanto, K. Arai, Electric wheelchair control with gazedirection and eye blinking, in: Proceedings
of the 14th International Sympo-sium on Artificial Life and Robotics, AROB, Oita, Japan, February 5–7, 2009,pp. 400–436
[25] J.Y. Long, Y. Li, H. Wang, T. Yu, J. Pan, F. Li, A hybrid brain com-puter interface to control the direction and speed of a simulated or realwheelchair, IEEE Trans. Neural Syst. Rehabil. Eng. 20 (5) (2012) 720–729
[26] R. Barea, L. Boquete, M. Mazo, E. Lopez, L.M. Bergasa, EOG guidance of awheelchair using neural networks, in: 15th International Conference onPattern Recognition, ICPR, vol. 4, Barcelona, Spain, 2000, pp. 668–671,
[27] A. Phinyomark, C. Limsakul, A review of control methods for elec-tric power wheelchairs based on electromyography signals with specialemphasis on pattern recognition, IETE Tech. Rev. 28 (4) (2011) 316–326.
[28] Zecca M., Micera S., Carroza M., Dario P., “Control Of
Multifunctional | Prosthetic | Hands | By | Processing | The
Electromyographic Signal”, Critical Reviews™ in Biomedical Engineering. Vol. 30, pp. 459 485.2002.

[29] Garcia, D., Espinoza, M., J., «Avances en prótesis: una mirada al presente y al futuro,» Revista Médica Clínica Las Condes, vol. 25, nº 2, pp. 281-285, 2014.
[30] T. Bionics, «Touch Bionics,» 2015. [En línea]. Available: http://www.touchbionics.com/products/active-prostheses/ilimb-ultra. [Último acceso: 21 07 2015].
[31] B. Peerderman, «Myoelectric forearm prostheses:
State of the art from a user-centered perspective,» Journal of rehabilitation research and development, vol. 48, nº 6, pp. 719-738, 2011.
[32] Loera Perez., E., A., «Proyecto E-Nable Sobre El Desarrollo De Prótesis Mecánicas,» Universidad Autonama de Nuevo Leon.
[33] Richard L. Drake, A. Wayne Vogl, Adam W. Mitchell. Anatomía para estudiantes, Barcelona: Elsevier, 2010.
[34] | Schunke, | Shulte, | Shumacher, | Voll, | Wesker.,
PROMETHEUS Texto y Atlas de Anatomía, Panaericana, 2005.
[35] John a. Kiernan, lippincott., W., wilkins.,W., Kluwer., H., El sistema nervioso humano: Una perspectiva anatómica, Barcelona: Lippincott Williams and Wilkins. Wolters Kluwer Health, 2009.
[36] Zecca M., Micera S., Carroza M., Dario P, «Control Of
Multifunctional | Prosthetic | Hands | By | Processing | The
Electromyographic Signal,» Critical Reviews™ in Biomedical Engineering, vol. 30, pp. 459-485, 2002.
[37] Ajiboye. A. B., Weir. R. F., «A heuristic fuzzy logic approach to EMG pattern recog-nition for multifunctional prosthesis control,» IEEE Trans. Neural Syst. Rehabil.Eng, vol. 13, nº3, p. 280–291, 2005.
[38] F.V.G. Tenore, A. Ramos, A. Fahmy, S. Acharya, R. etienne-Cummings,N.V. Thakor, «Decoding of individuated finger movements using surfaceelectromyography,» IEEE Trans. Biomed. Eng, vol. 56, nº 5, p. 1427–1434, 2009.
[39] L.J. Hargrove, G. Li, K. Englehart, B. Hudgins, «Principal components analysispreprocessing for improved classification accuracies in pattern-recognition-based myoelectric control,» IEEE Trans. Biomed. Eng, vol. 56, nº 5, p. 1407–1414, 2009.
[40] Maria Hakonena, Harri Piitulainenb, Arto Visalaa, «Current state of digital signal processing in myoelectric interfaces
and related applications,» Biomedical Signal Processing and Control, pp. 334-359, 2015.
[41] D.F. Stegeman, H.J. Hermens, «Standards for surface electromyography,» in:The European Project Surface EMG for Non-Invasive Assessment of Muscles(SENIAM), 2007.
[42] G. Li, Y. Li, L. Yu, Y. Geng, « Conditioning and sampling issues of EMG signals in motion recognition of multifunctional myoelectric prostheses,» Ann. Biomed. Eng, vol. 39, nº 6, p. 1779–1787, 2011.
[43] A. Carrera, «Elasticidad y dureza de los huesos»,
Universidad | Tecnológica | de | Equinoccial, | Escuela | de
Odontologia, 2013.
[44] Jaramillo Pineda, V. A., Pineda, J., & Garcia Arias, L.F., «Design of an automatic voice controlled system and remote control», IEEE Explora, pp. 1-5, 2014.
[45] Galvis Giraldo, G., Garcia Arias, L.F., & Jaramillo Pineda,
V. A., «Diseño de una prótesis mioeléctrica de miembro superior de código abierto».
[46] Davidson, Andrew. (2013). Killer game programming in java [web] recuperado de http://fivedots.coe.psu.ac.th/~ad/jg/nui055/
[47] Matney, Lucas. (2016). Huawei unveils its own mobile VR
headset | [web] | recuperado | de:
https://techcrunch.com/2016/04/15/huawei-unveils-its-own-mobile-vr-headset/
[48] Broida, Rick. (2015). See the world in VR with Google
Cardboard | and | Street | View | [web] | recuperado | de:
https://www.cnet.com/how-to/see-the-world-in-vr-with-google-cardboard-and-street-view/
[49] Tr4nsduc7or. (2014). Tutorial de Arduino y MPU-6050 [web]
recuperado | de: | http://robologs.net/2014/10/15/tutorial-de-
arduino-y-mpu-6050/

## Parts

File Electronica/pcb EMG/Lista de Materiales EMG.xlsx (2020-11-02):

Lista de Materiales EMG
Cantidad | Descripción | Referencia en Diseño
1 | SPECIAL_FUNCTION, INA126P | U1
2 | RESISTOR, 15kOhm | R7, R14
2 | RESISTOR, 510Ohm | R11, R12
3 | RESISTOR, 100kOhm | R3, R4, R19
1 | RESISTOR, 20kOhm | R20
1 | HEADERS_TEST, HDR1X3 | J2
1 | HEADERS_TEST, HDR1X3 | J3
1 | HEADERS_TEST, HDR1X2 | J1
6 | CAPACITOR, 1uF | C4, C5, C6, C7,C9, C12
2 | CAPACITOR, 0.1uF | C1, C2
2 | RESISTOR, 180Ohm | R15, R16
3 | OPAMP, LF353P | U2, U3, U4
2 | RESISTOR, 500Ohm | R2, R17
1 | RESISTOR, 10kOhm | R8
1 | POTENTIOMETER, 10kOhm | R1

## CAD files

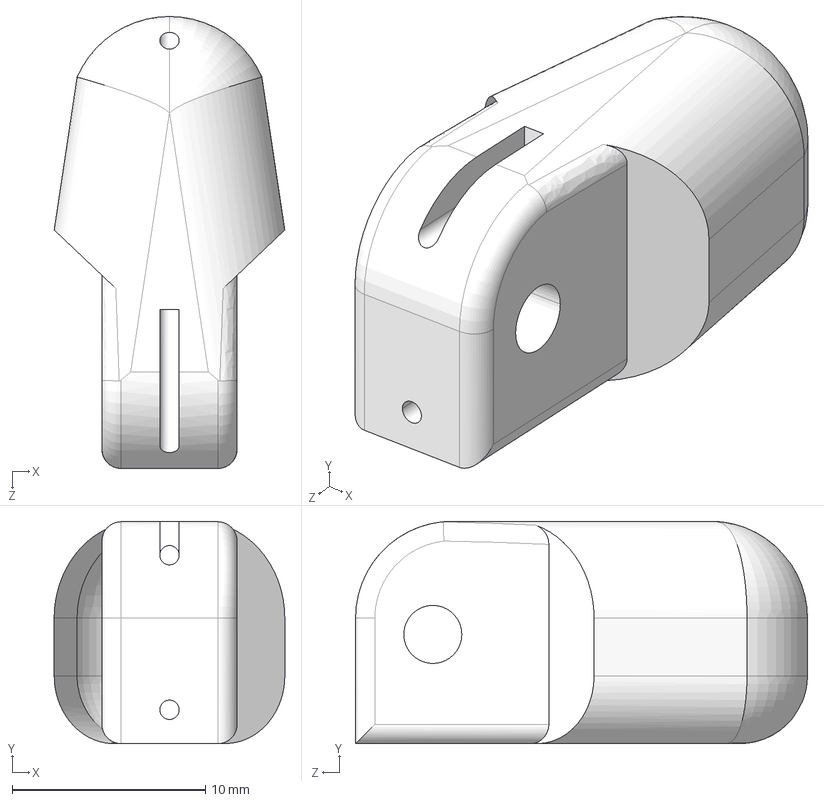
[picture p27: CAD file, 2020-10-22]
MULPOS Piezas/1 meñique/Falange_Distal_Meñ.STEP
11.9 x 11.5 x 23.4 mm

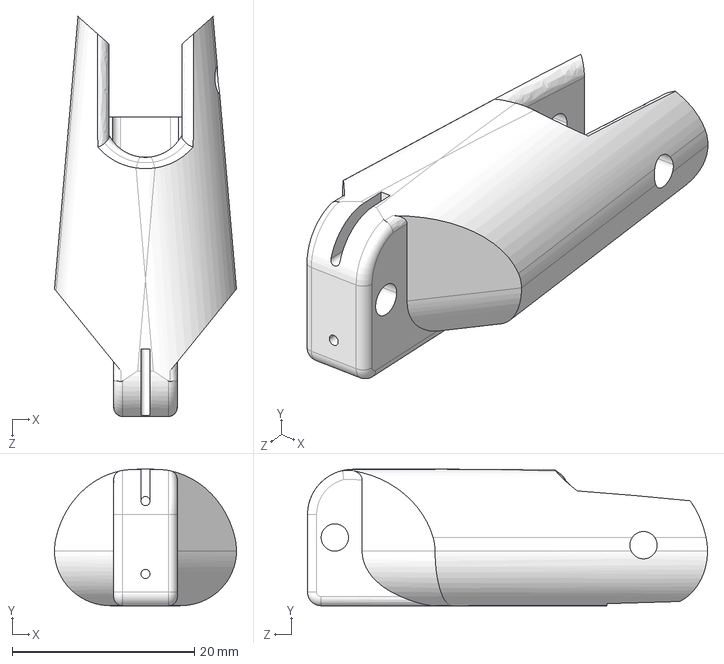
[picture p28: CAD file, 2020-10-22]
MULPOS Piezas/2 anular/Falange_Proximal_An.STEP
20.0 x 15.0 x 43.9 mm

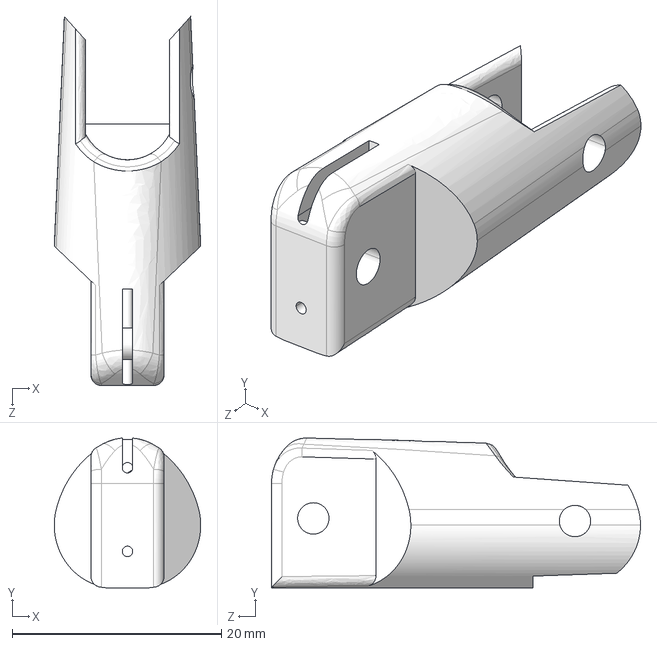
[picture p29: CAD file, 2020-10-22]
MULPOS Piezas/3 medio/Falange_Media_Med.STEP
14.0 x 14.3 x 35.3 mm

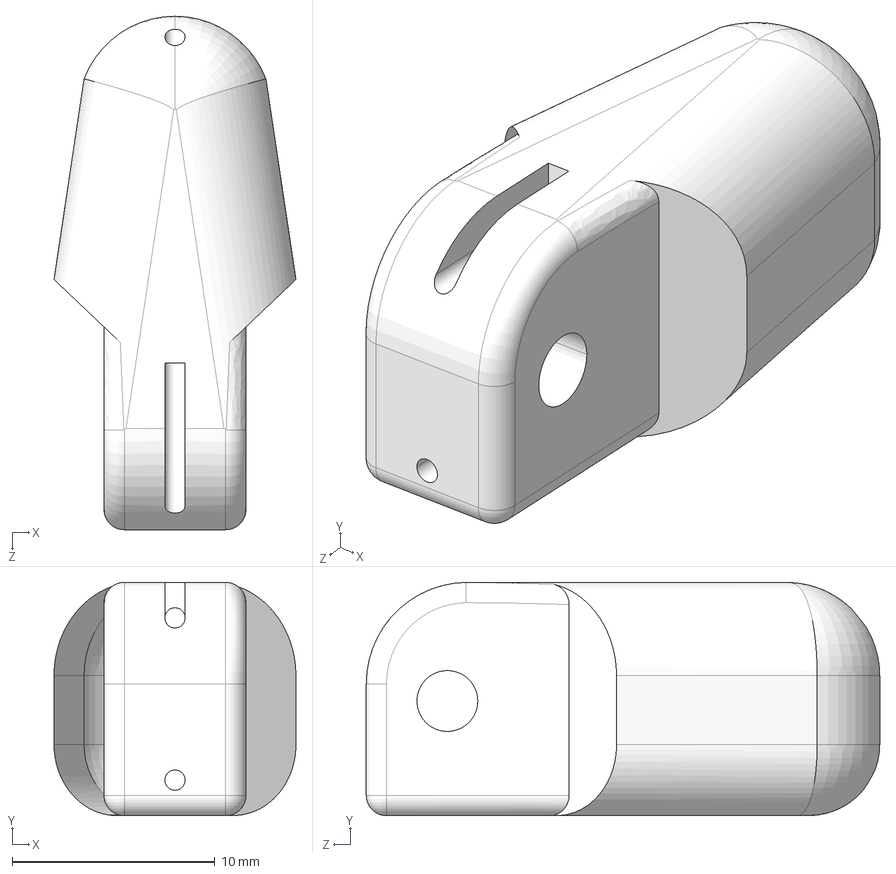
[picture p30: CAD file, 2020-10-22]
MULPOS Piezas/4 indice/Falange_Distal_Ind.STEP
11.9 x 11.5 x 25.3 mm

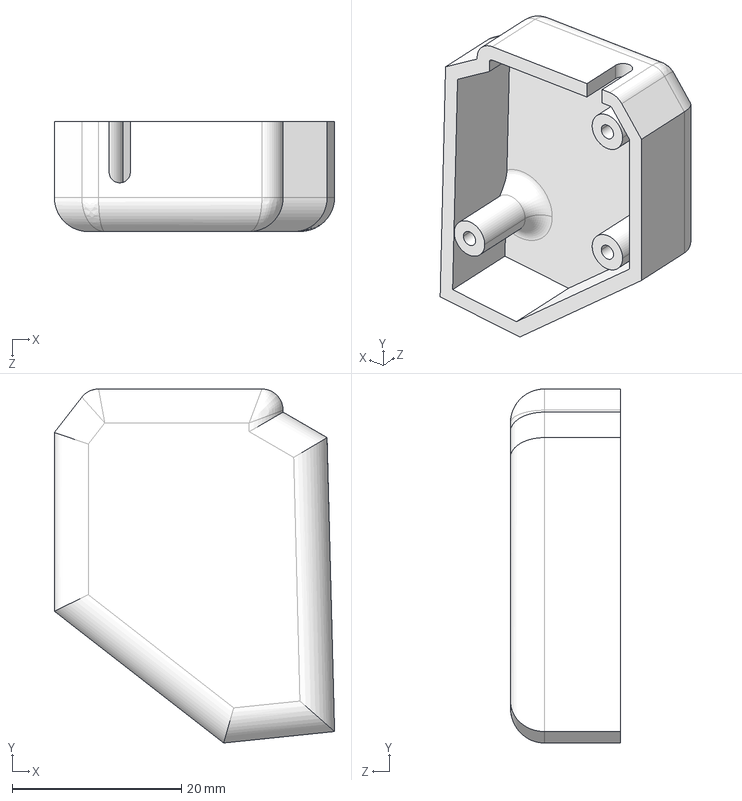
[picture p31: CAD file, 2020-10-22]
MULPOS Piezas/5 pulgar/tapa_palma_interior_pulgar.STEP
33.1 x 41.8 x 13.0 mm

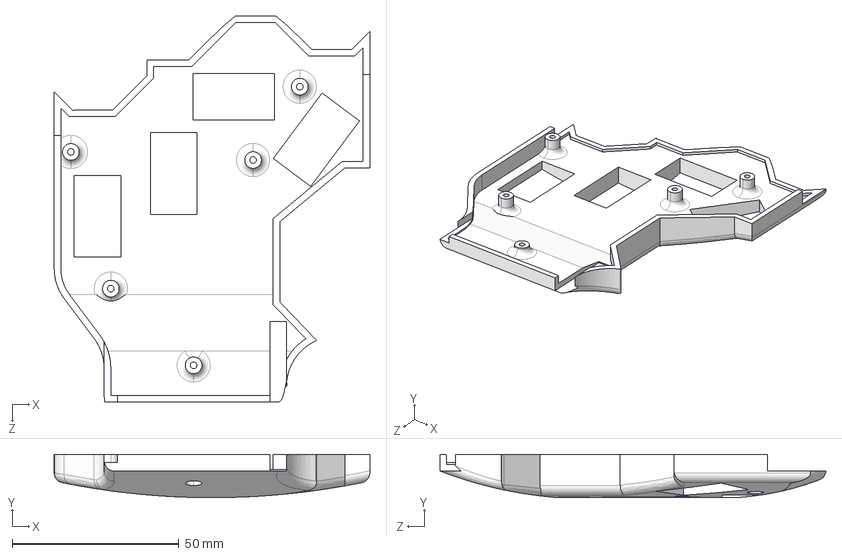
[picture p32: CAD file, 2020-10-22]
MULPOS Piezas/6 palma/tapa_palma_posterior.STEP
94.7 x 13.0 x 115.8 mm

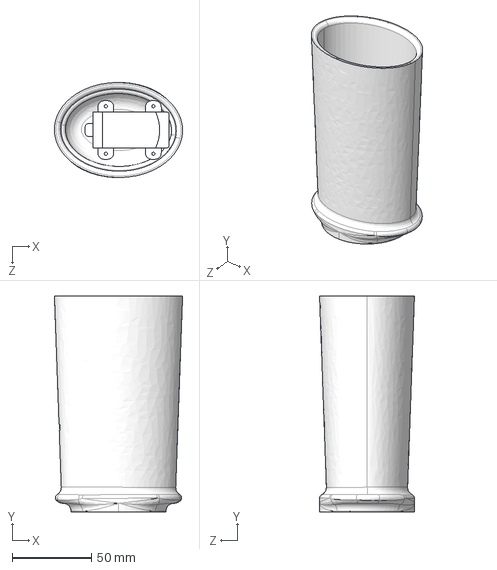
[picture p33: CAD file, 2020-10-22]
MULPOS Piezas/7 muñeca/muñeca_pron_supr.STEP
81.0 x 136.4 x 60.0 mm

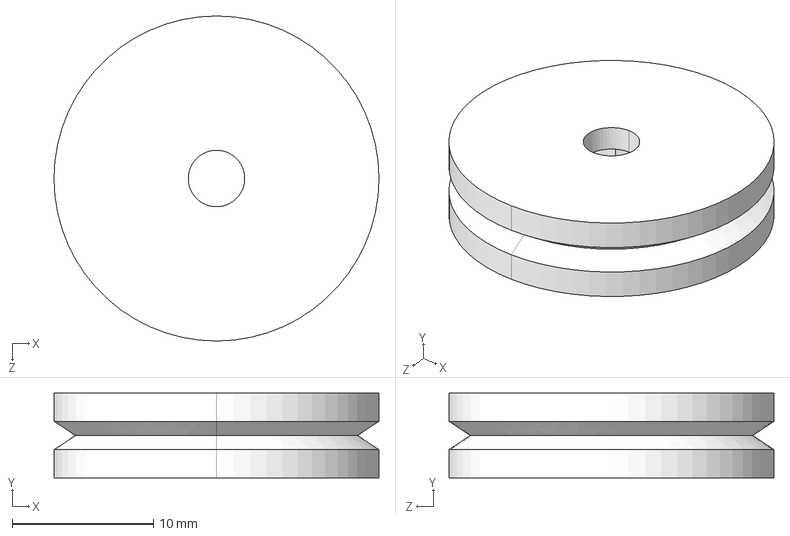
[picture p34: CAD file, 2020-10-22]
MULPOS Piezas/8 acoples/acople_servo_dedos.STEP
23.0 x 6.00 x 23.0 mm

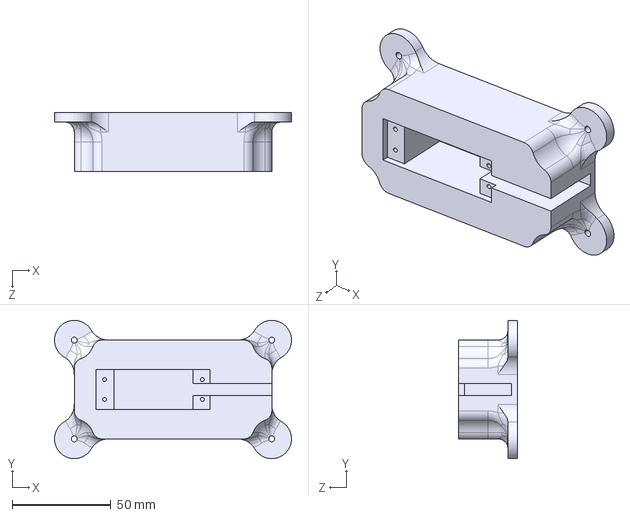
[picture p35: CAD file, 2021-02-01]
STARPI/Firmware/Vision VR STARPI/camera_mount_3D_files/base_yaw.STEP
120.0 x 70.0 x 30.0 mm

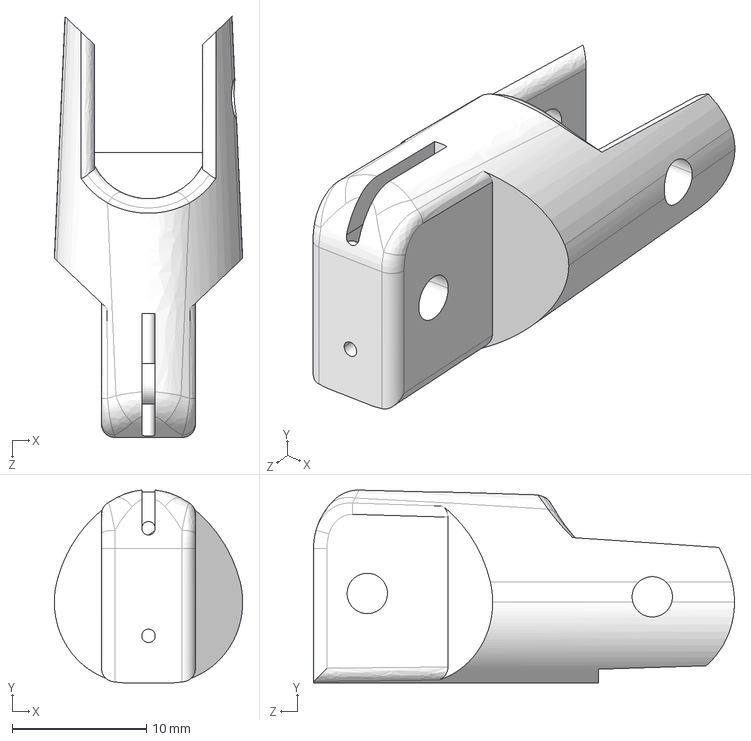
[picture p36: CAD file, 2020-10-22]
MULPOS Piezas/1 meñique/Falange_Media_Meñ.STEP
14.0 x 14.3 x 31.3 mm

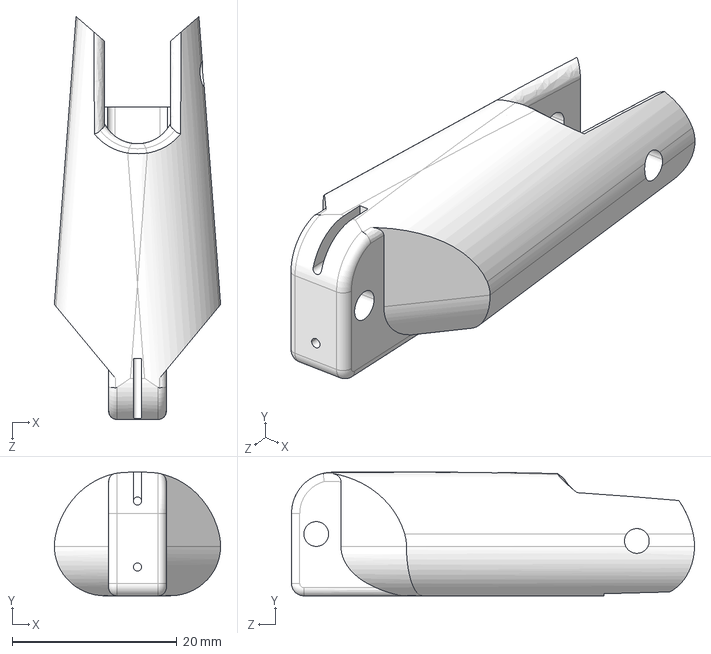
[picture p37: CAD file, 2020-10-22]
MULPOS Piezas/3 medio/Falange_Proximal_Med.STEP
20.2 x 15.0 x 48.9 mm

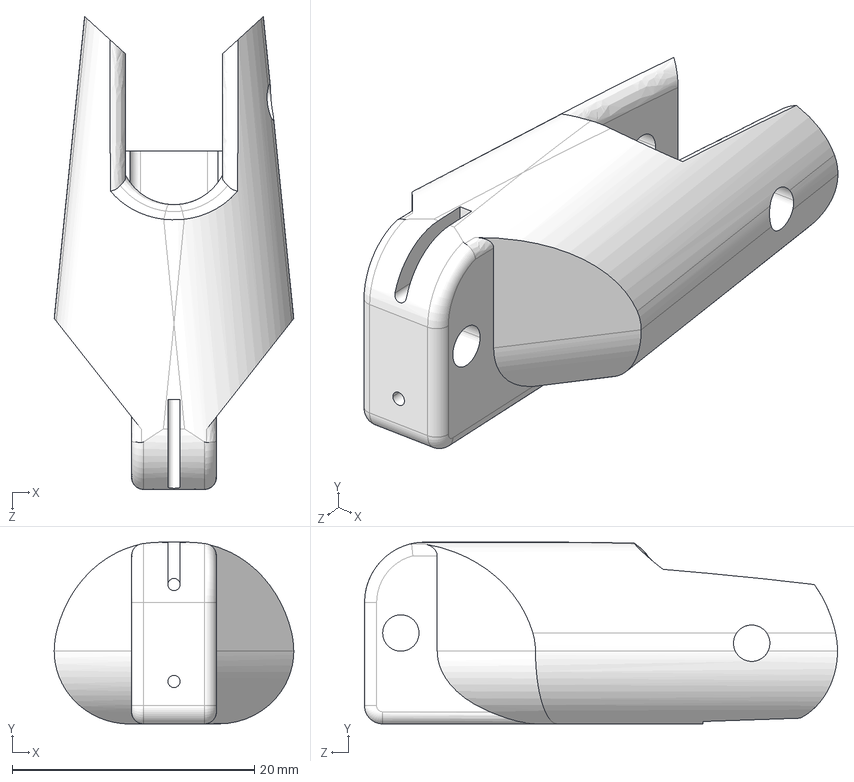
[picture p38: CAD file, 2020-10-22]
MULPOS Piezas/5 pulgar/Falange_Proximal_Pul.STEP
19.8 x 15.0 x 39.0 mm

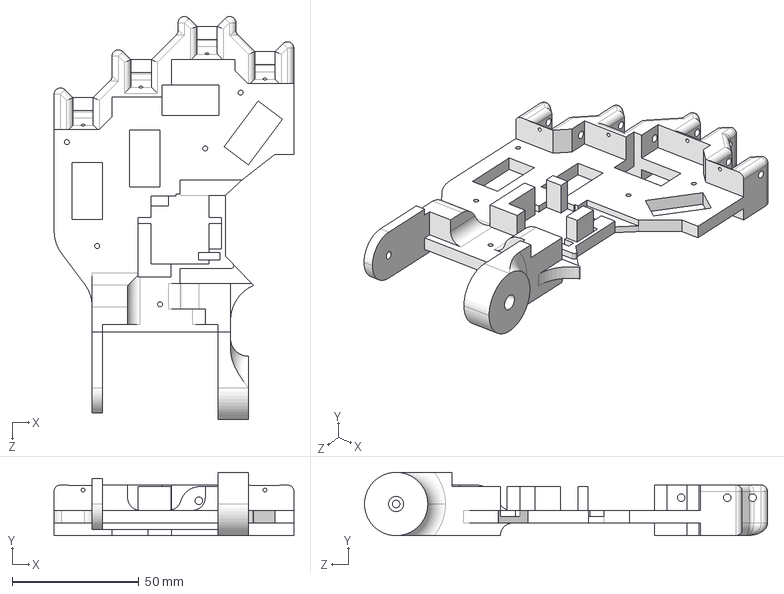
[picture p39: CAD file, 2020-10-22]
MULPOS Piezas/6 palma/palma.STEP
94.7 x 25.0 x 159.1 mm

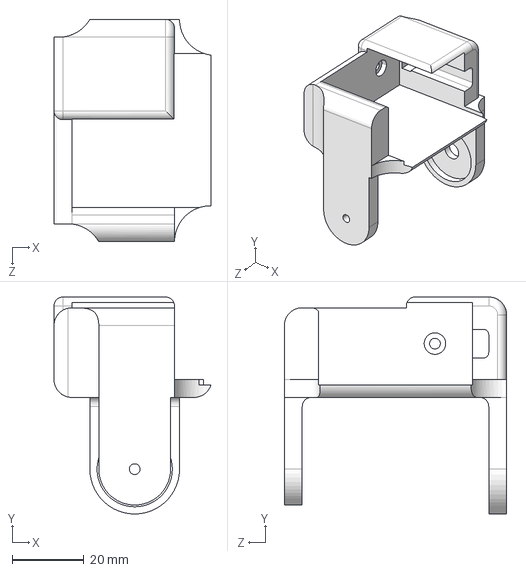
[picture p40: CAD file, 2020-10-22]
MULPOS Piezas/7 muñeca/muñeca_flex_exten.STEP
43.8 x 60.5 x 62.0 mm

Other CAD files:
MULPOS Piezas/2 anular/Falange_Distal_An.STEP
MULPOS Piezas/4 indice/Falange_Proximal_Ind.STEP
MULPOS Piezas/8 acoples/tapa_servo_antebrazo.STEP
STARPI/Firmware/Vision VR STARPI/camera_mount_3D_files/base_webcam.STEP
MULPOS Piezas/1 meñique/Falange_Distal_Meñ.STL
MULPOS Piezas/1 meñique/Falange_Media_Meñ.STL
MULPOS Piezas/1 meñique/Falange_Proximal_Meñ.STEP
MULPOS Piezas/1 meñique/Falange_Proximal_Meñ.STL
MULPOS Piezas/2 anular/Falange_Distal_An.STL
MULPOS Piezas/2 anular/Falange_Media_An.STEP
MULPOS Piezas/2 anular/Falange_Media_An.STL
MULPOS Piezas/2 anular/Falange_Proximal_An.STL
MULPOS Piezas/3 medio/Falange_Distal_Med.STEP
MULPOS Piezas/3 medio/Falange_Distal_Med.STL
MULPOS Piezas/3 medio/Falange_Media_Med.STL
MULPOS Piezas/3 medio/Falange_Proximal_Med.STL
MULPOS Piezas/4 indice/Falange_Distal_Ind.STL
MULPOS Piezas/4 indice/Falange_Media_Ind.STEP
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

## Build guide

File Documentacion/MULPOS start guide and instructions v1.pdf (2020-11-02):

## MULPOS start guide and instructions v1 https://www.moveorobotics.com/ https://github.com/gigalgi/Mulpos_Project

## 1. Prótesis I. descargue los archivos STL e imprima (si desea hacer modificaciones también encontrara los archivos step de cada

pieza para modificarla a su gusto).

## II. Materiales prótesis

- prótesis MULPOS
- EMG (ver sección del EMG)
- smartphone con sistema andorid superior a 4.2
- bluetooth hc-05 o hc-06
- arduino (cualquier referencia)
- tornillo 3mm con tuerca
- tornillo para madera 2mm x 15mm
- nailon
- 6 servos sg90 o mg90s para los dedos
- 3 servos mg995 para la muñeca

## III. Ensamble

`

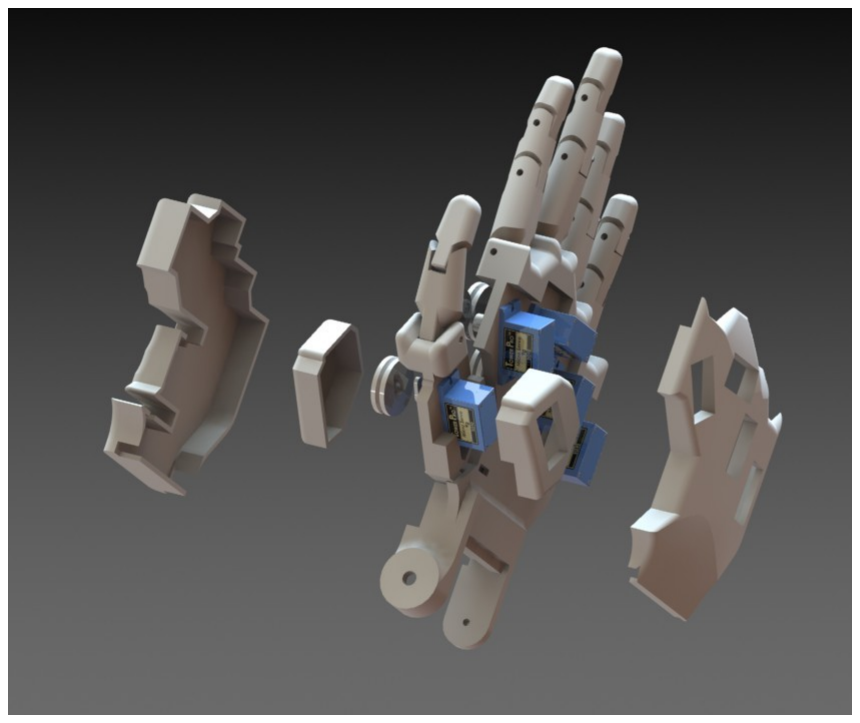
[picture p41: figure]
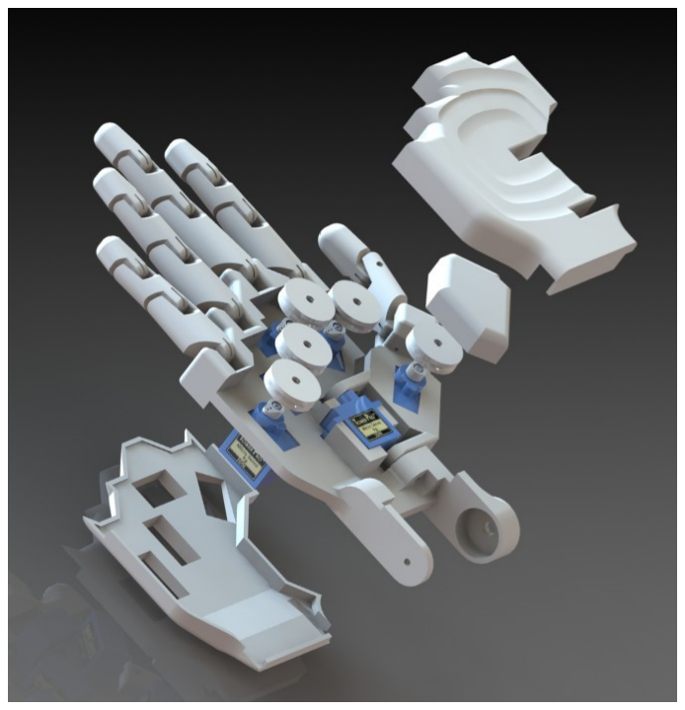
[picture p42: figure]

Use tornillos tornillos para madero de 1-2 mm de diámetro y 15mm de longitud para atornillar las tapas que cubren los servos.

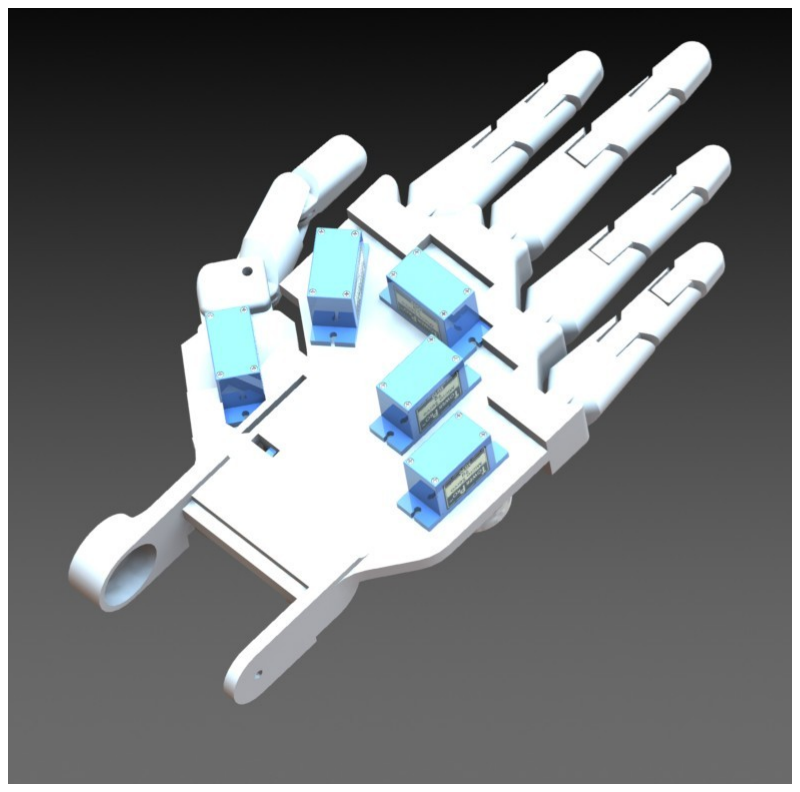
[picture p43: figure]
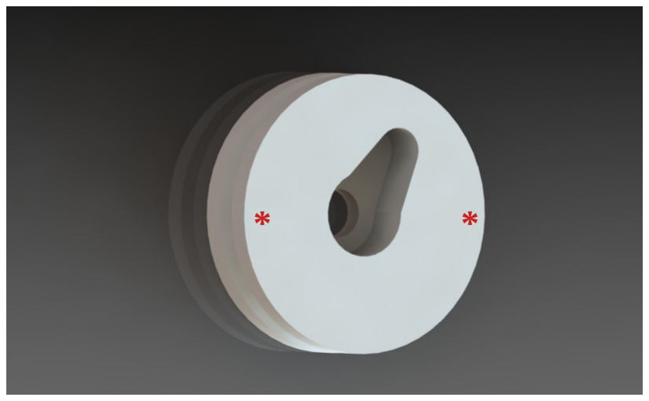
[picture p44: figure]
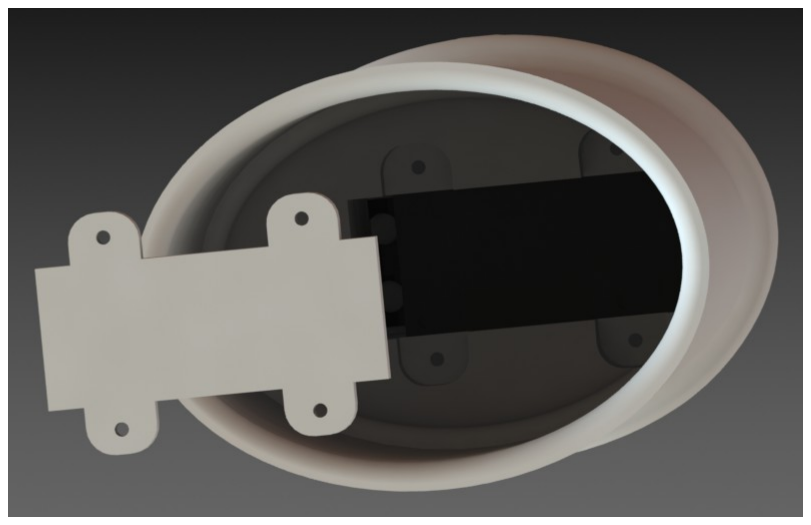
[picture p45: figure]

`Espacio para servo pronación y supinación.

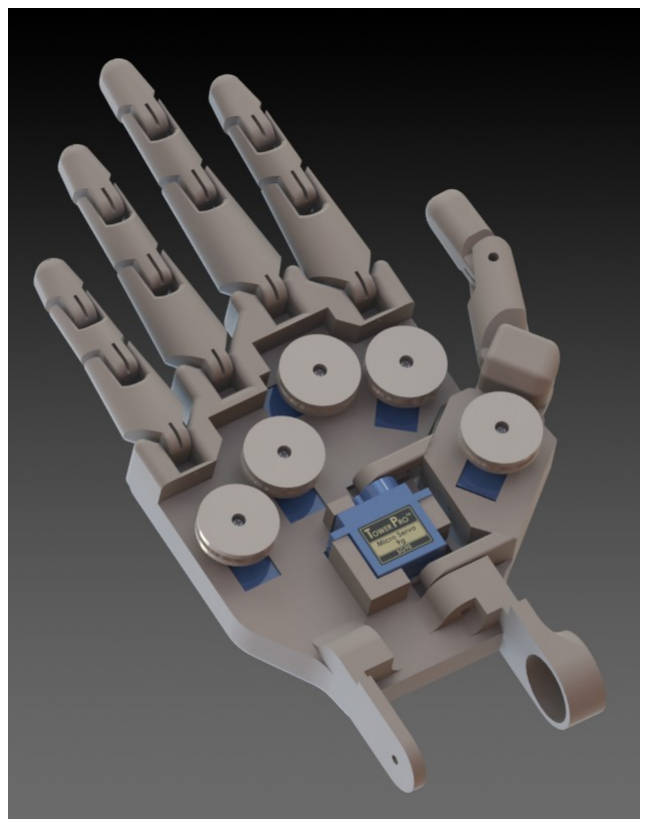
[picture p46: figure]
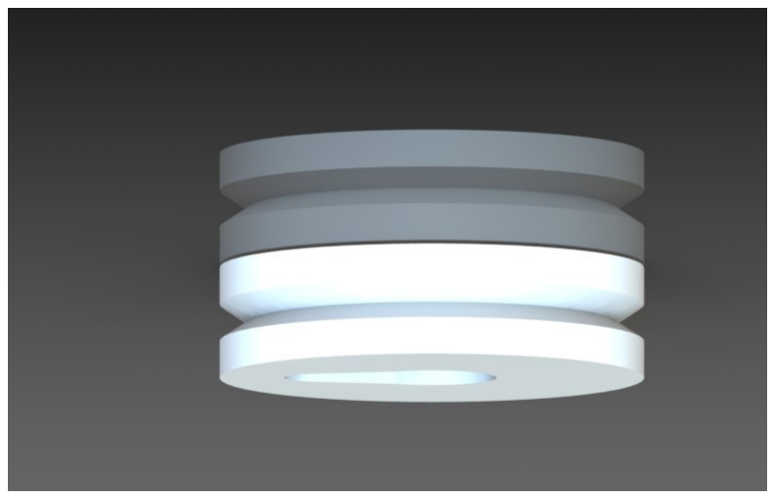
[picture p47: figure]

Poleas para controlar la flexión y extensión de los dedos, al colocar los servos y las poleas como se ve en la figura 4 fije el servo a 90 grados y realice 2 agujeros pequeños paralelos con la horizontal para atar el nailon que flexionara los dedos.

Para ensamblar los dedos inserte tornillos de 3mm de diámetro después Tome un trozo de nailon y pase por los agujeros de cada falange cada dedo tiene dos agujeros uno en el frente paralelo a la palma y atrás paralelo a el reverso de la mano luego pase ambos hilos por el agujero en la palma justo debajo de cada dedo y ate a las poleas.

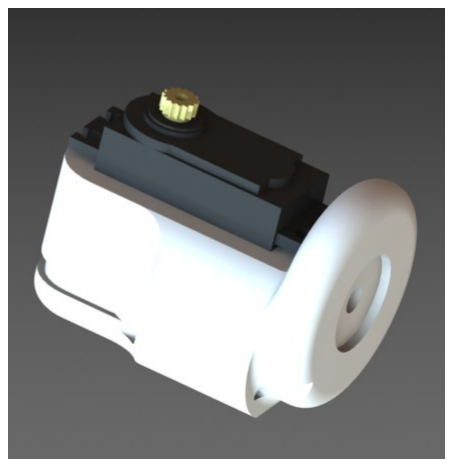
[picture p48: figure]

Atornille esta pieza con
la pieza de la figura
anterior por medio del
agujero y luego coloque
el servo.

Use tornillos de 3mm con tuerca para unir las piezas de la muñeca

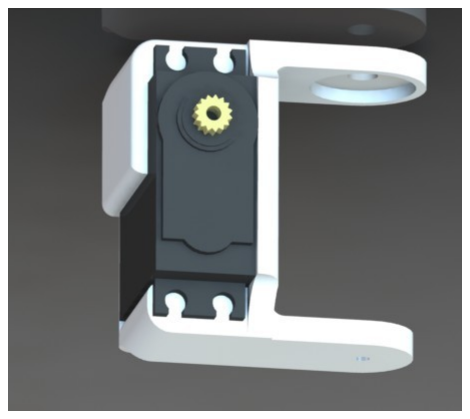
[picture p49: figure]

Atornille esta pieza a la
anterior y la la mano use
los bujes circulares que
trae el servo para estas
uniones.

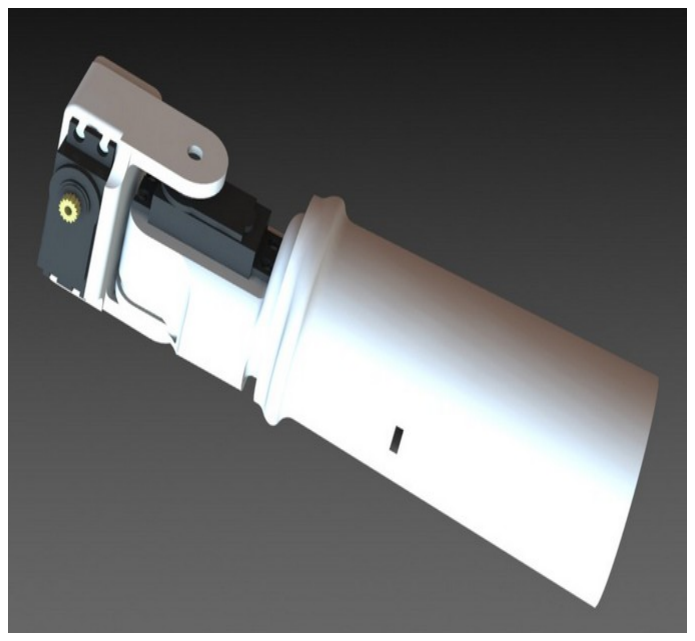
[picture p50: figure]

## Peso aprox de prótesis usando ABS

- peso muñeca 265 gr
- peso mano 232 gr
- peso servos mano 54 gr
- peso servo muñeca 165 gr
- peso con densidad completa 716 gr
- peso con densidad media 517 gr

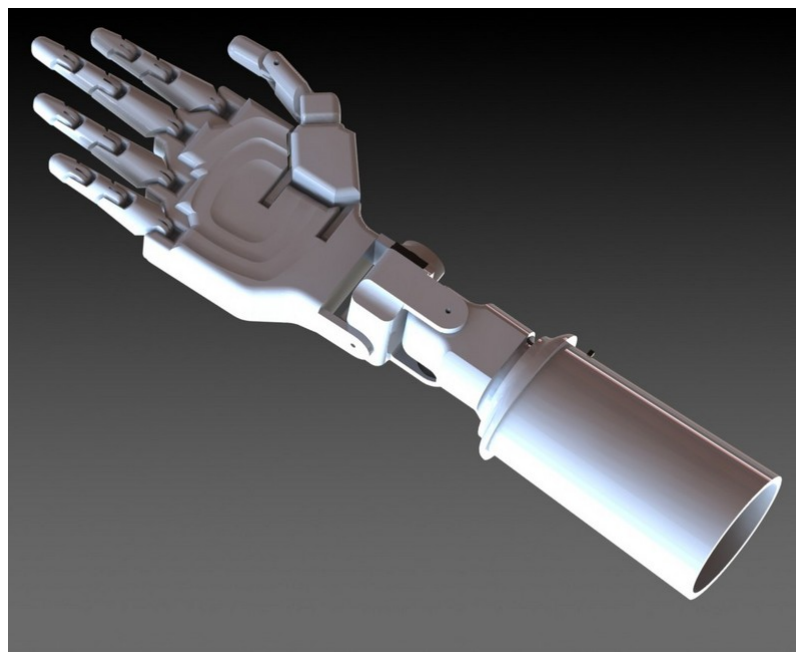
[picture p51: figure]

### 2. Electromiografo (Refiérase a la carpeta “Electronica” para PCB y Cerigrafia)

## I. Materiales

Lista de Materiales EMG
Cantidad | Descripción | Referencia en Diseño
1 | SPECIAL_FUNCTION, INA126P | U1
2 | RESISTOR, 15kOhm | R7, R14
2 | RESISTOR, 510Ohm | R11, R12
3 | RESISTOR, 100kOhm | R3, R4, R19
1 | RESISTOR, 20kOhm | R20
1 | HEADERS_TEST, HDR1X3 | J2
1 | HEADERS_TEST, HDR1X3 | J3
1 | HEADERS_TEST, HDR1X2 | J1
6 | CAPACITOR, 1uF | C4, C5, C6, C7,C9, C12
2 | CAPACITOR, 0.1uF | C1, C2
2 | RESISTOR, 180Ohm | R15, R16
3 | OPAMP, LF353P | U2, U3, U4
2 | RESISTOR, 500Ohm | R2, R17
1 | RESISTOR, 10kOhm | R8
1 | POTENTIOMETER, 10kOhm | R1

## II. Circuito

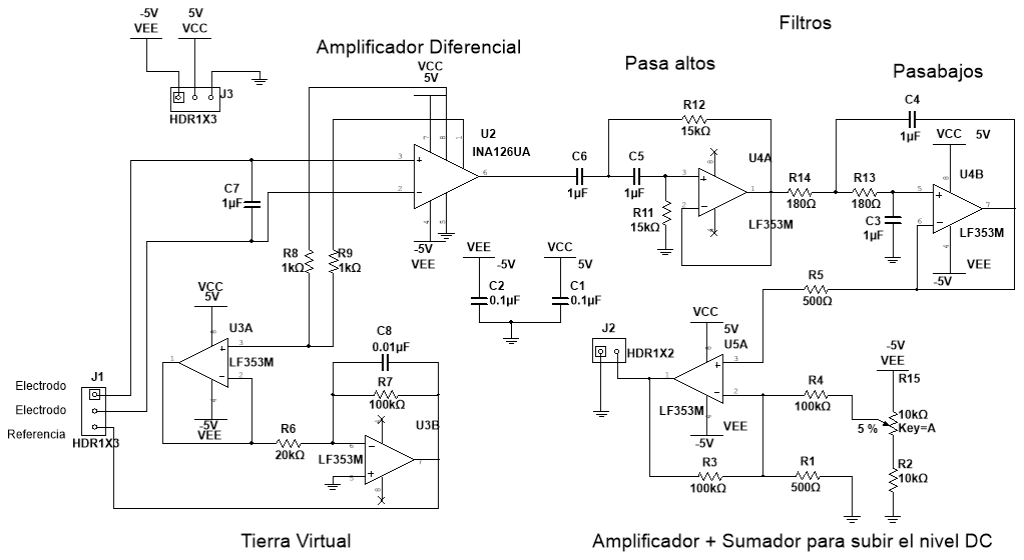
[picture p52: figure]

## III. Referencia para preparar y posicionar el electrodo - https://learn.adafruit.com/getting-started-with-myoware-

muscle-sensor/placing-electrodes (https://learn.adafruit.com/getting-started-with-myoware-muscle-sensor/placing-electrodes)

## 3. Electrónica de control (diagrama de conexiones)

- Para alimentar el circuito use una batería de 2 celdas preferiblemente adicione un regulador de 5 voltios para los servos de la mano si usa una batería con voltaje mayor a 5V

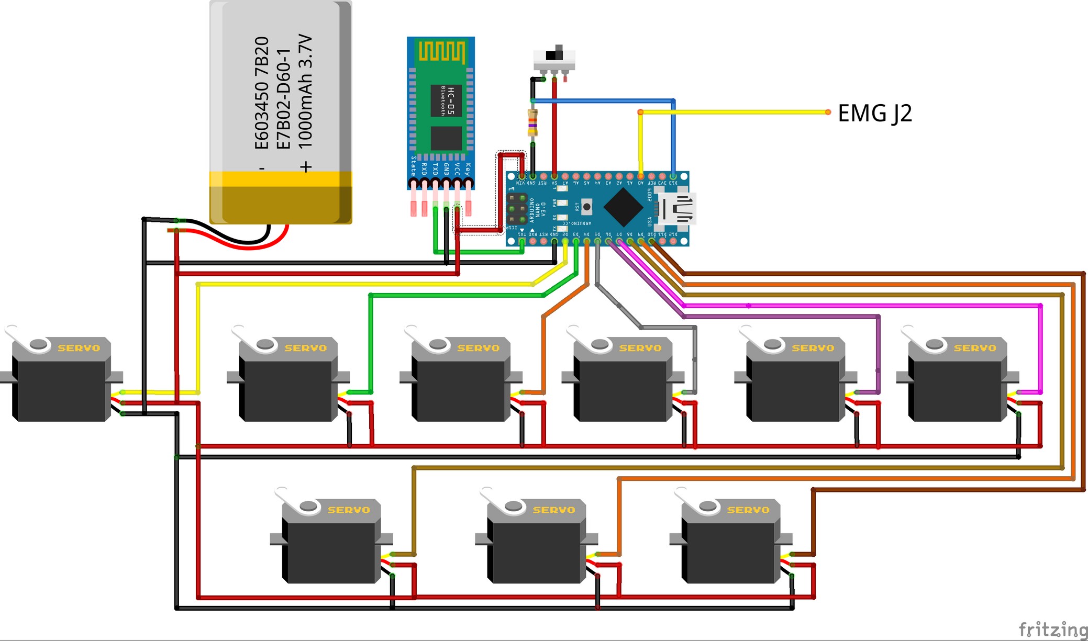
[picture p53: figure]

## 4. Selección Modo De Control para APP o EMG

I. En el apartado de 3.Electrónica de Control, vera en el circuito un switch este controla el modo en que la prótesis se controla si este esta en alto la prótesis funcionara en el modo App o para ser usada Con el proyecto STARPI(Para saber mas de STARPI refiérase a su documentación). Si lo pone en bajo esta entrara en el modo de control por EMG.

## 5. Control por EMG

I. Al usar este modo puede elegir otro sub-modos de control con pulsos eléctricos al tensionar el musculo con fuerza rápidamente dentro de un periodo de 3 segundos puede modificar este tiempo en el código fuente. Para referenciar el valor máximo del pulso por favor cargue el código emg_calibracion obtenga el valor máximo del pulso acorde a su brazo y agréguelo en el firmware mulpos. En el código encontrar donde ubicar este valor indicado por los comentarios del mismo en la sección de variables de control.

II. Al iniciar el sistema espera la selección del modo de inicio 1 pulso para el modo de agarre, 2 pulsos para modo de giro de muñeca, 3 pulsos pone la prótesis en posición inicial, dispone de 2 segundos para realizar estos pulsos si desea ampliar el tiempo puede modificarlo en el código fuente.

- Modo de agarre: el modo agarre tiene 4 submodos agarre normal con todos los dedos y agarre pinza usando el pulgar y el indice, soltar y volver al menú principal.
- Al haber seleccionado el modo agarre entre por defecto al modo agarre normal,para iniciar la sujeción mantenga el musculo presionado y relájelo cuando desee que la mano pare de cerrase, si desea abrir la mano realice 2 pulsaciones rápidas.
- Modo agarre con pinza: entre en este modo realizando 1 contracción rápidas funciona igual el modo agarre normal, si desea volver al modo agarre normal realice una pulsación rápidas nueva.
- Modo soltar: realice dos contracciones rápidas.
- Salir del modo agarre: realice 3 pulsaciones rápidas.
- Modo giro muñeca:
- Al Seleccionar este modo la muñeca se posiciona por defecto en el centro para girar en sentido horario realice 1 pulsación y giro en sentido antihorario realice 2 pulsaciones o contracciones.
- Modo giro horario: Si se encuentra en este modo realice una contracción y mantengala la prótesis comenzara a girar si desea detenerse detenga la contracción relajando el musculo, para volver al centro realice 1 contracción rápida. Si desea cambiar el sentido del giro a antihorario realice 2 contracciones rápidas.
- Modo giro antihorario: Si se encuentra en este modo realice una contracción y mantengala la prótesis comenzara a girar si desea detenerse detenga la contracción relajando el musculo, para volver al centro realice 2 contracción rápida. Si desea cambiar el sentido del giro a antihorario realice 1 contracción rápida.
- Modo Valores por defecto
- si esta en el menú de inicio realice tres pulsaciones para regresar la prótesis a una posición de inicio.

## 6. Control por App I. Configuración inicial - Icono

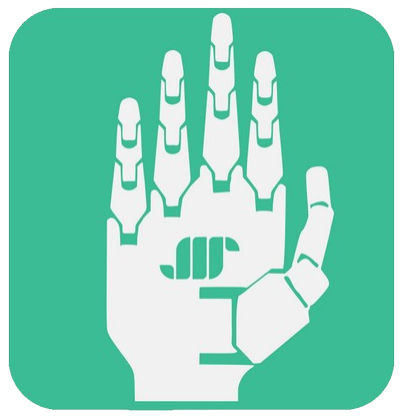
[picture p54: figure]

Este es el icono que vera al instalar la aplicación.

## - Interface y Uso

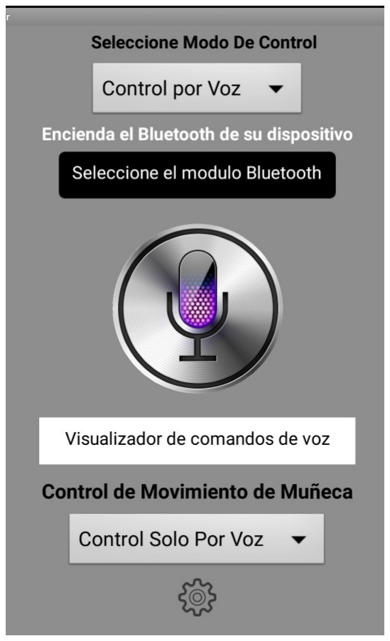
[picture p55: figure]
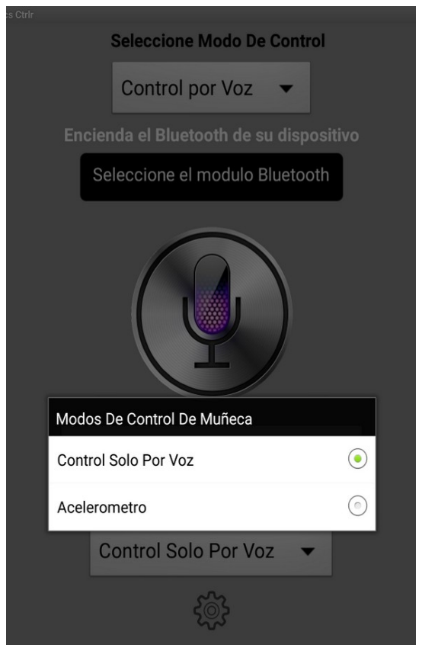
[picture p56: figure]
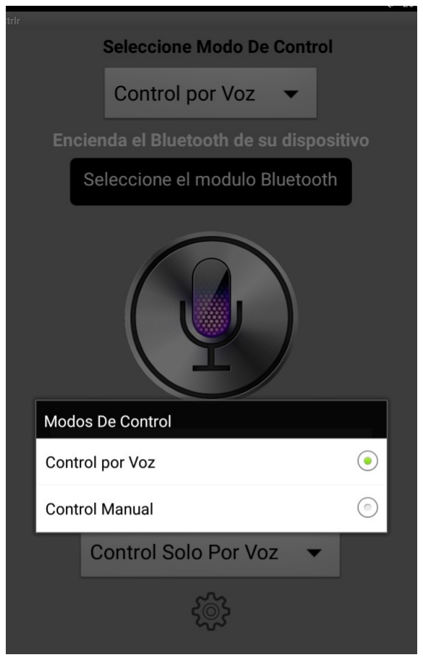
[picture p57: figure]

1) Active el Bluetooth en su dispositivo y emparejarlo con el Bluetooth de MULPOS (hc-05 o hc-06).
2) Abra la aplicación al iniciar se encontrara con los visto en la figura 1 presione el botón “seleccionar modulo Bluetooth”luego seleccione el a conectarse.
3) Deberá aparecer el mensaje Bluetooth conectado.
4) El botón para comandos de voz quedara activo para ver los comandos disponibles referirse a la tabla de comandos de voz disponible a continuación:

Lista de comandos por voz

Manado por voz | Comando a enviar
saludar | j
despedirse | j
sujetar | h
soltar | 6
bien | k
ok | m
centro | l
derecha | o
izquierda | p
arriba | q
abajo | n
ahí | r
mal | t
sujetar suave | u
sujetar con los dedos | v
jodete | z
cerrar f1 | c
abrir f1 | 1
cerrar f2 | d
abrir f2 | 2
cerrar f3 | e
abrir f3 | 3
cerrar f4 | f
abrir f4 | 4
cerrar f5 | g
abrir f5 | 5

5) Puede cambiar el control de la muñeca en el menú desplegable control de movimiento de muñeca, encontrar dos opciones modo fijo es decir solo control por comandos de voz o control con acelerometro( ver figura 2).
6) para cambio de modo control vera otro menú desplegable seleccione control manual para controlar la prótesis con botones, acelerometro y un padtactil como vera a continuación. NOTA: el Bluetooth se desconecta al cambiar el modo de control conectarse nuevamente igual que lo hizo al inicio debe conectarlo nuevamente cada vez que cambie de modo de control.

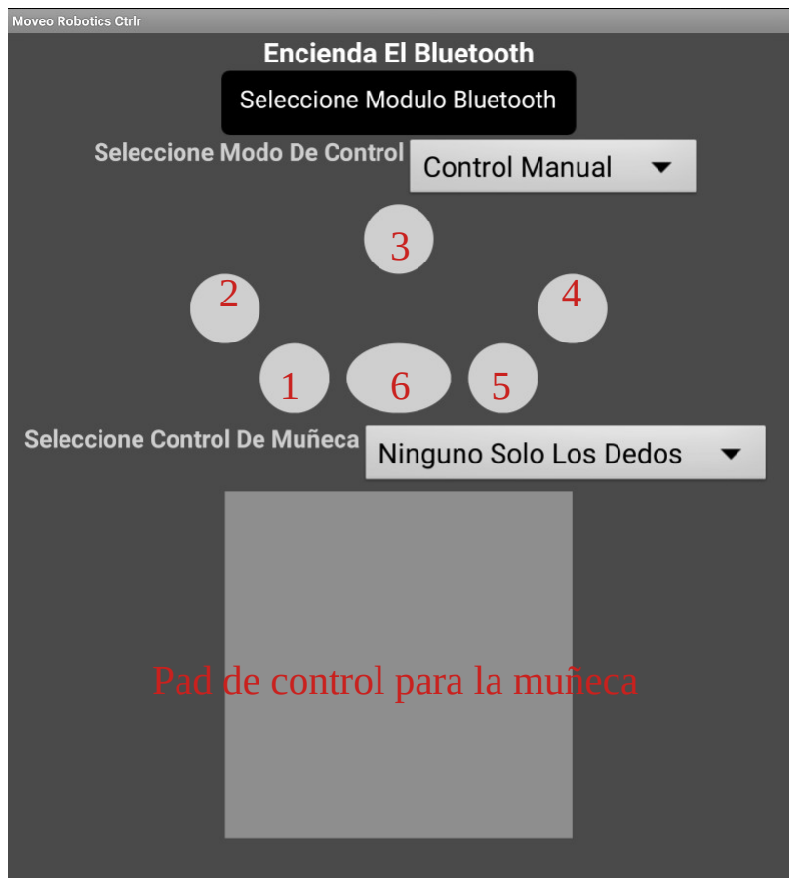
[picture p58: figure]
Pad de control para la muñeca
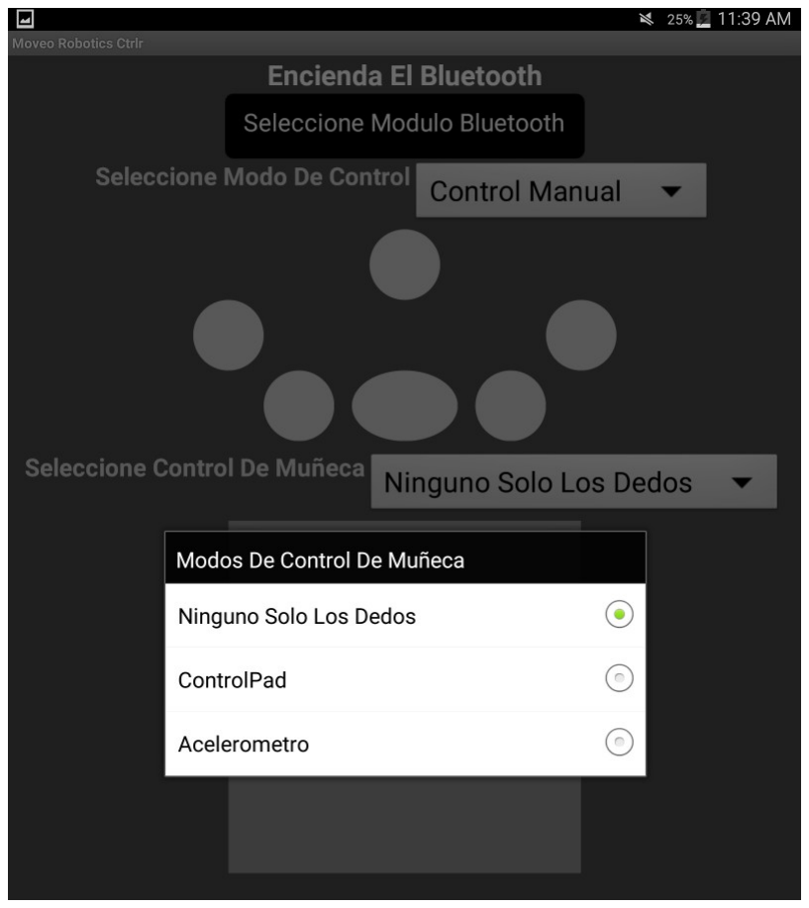
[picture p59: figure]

7) El botón 1 controla el menique, 2 el indice, 3 medio, 4 anular, 5 pulgar; al presionar cualquier botón una vez el dedo se cierra para abrirlos presione nuevamente, el botón 6 abre y cierra todos dos dedos.
8) en el modo manual la muñeca cuenta con control por “acelerometro” y “controlPad”, por “acelerometro” este moverá la muñeca imitando la inclinación del teléfono en el modo “controlpad” mueve la muñeca en la dirección que mueve el dedo si desea volver al centro haga un toque al centro del pad y la muñeca regresa a su posición inicial.
9) el modo “ninguno solo los dedos” deja la muñeca fija en la ultima posición.

## 7. Para mas información visite nuestro sitio web www.moveorobotics.com o contáctenos a través email: support@moveorobotics.com

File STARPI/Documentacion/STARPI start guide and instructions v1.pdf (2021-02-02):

STARPI start guide and instructions v1 https://www.moveorobotics.com/starpihttps://github.com/gigalgi/Mulpos_Project/tree/main/STARPI

### 1. Prótesis

I. Descargue los archivos STL e imprima (si desea hacer modificaciones también encontrara los archivos step de cada pieza para modificarla a su gusto)
podra encontrar los archivos e instrucciones necesarios en https://github.com/gigalgi/Mulpos_Project

### 2. Aplicación de control servidor maestro de prótesis

I. Realice las conexiones de acuerdo al esquema de la sección “Client Section Controller”.

II. Cargue el firmware de control del proyecto MULPOS Mulpos_Project/Firmware/mulpos_firmware_v1.1.0.ino

III. Ejecute la aplicación de la carpeta Firmware/App Control STARPI/starpi_control_server.py con python3, esta corre a traves del puerto 3001

IV. Ejecute el servidor HTTP de node.js para el control de la emisión de la cámara web para la visión remota que encontrara en STARPI/Firmware/Vision VR STARPI/

### 1. Para ejecutar debe instar primero las dependencias con el

comando $ npm i

### 2. Para iniciar la app ejecute el comando $ npm start

3. La aplicación corre a través del puerto 3000.

`

V. Ejecute la app emitir.py con python 3 para la adquisición de imagen de la cámara la emisión de video al servidor.

VI. En esta misma carpeta STARPI/Firmware/Vision VR STARPI/ encontrara los archivos 3D de la montura de la cámara para la visión remota

### 3. Control de muñeca

I. Realice las conexiones de acuerdo al esquema de la sección “Client Section Controller”.
II. Cargue el firmware que encontrara en la capeta “STARPI/ Firmware/Control Muneca/starpi_wrist_ctrl”.

III. Ajuste el acelero-metro en reveso de su

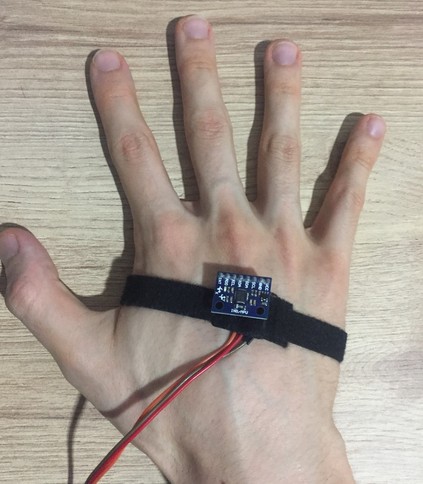
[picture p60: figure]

mano derecha como se ve en la imagen el
eje “x” debe estar paralelo a su dedo indice y el eje “y” perpendicular a este.

IV. Conecte vía usb a su maquina raspberry pi cliente o de su preferencia que controlara las acciones del cliente antes de energizar el dispositivo coloque su mano sobre una superficie plana para calibrar el acelero-metro al conectar el arduino al puerto usb este iniciara el programa y comenzara a calibrar el sensor la luz led del pin 13 se encenderá una vez se apague el proceso de calibración habrá terminado y empezar a enviar los datos por puerto serial al la aplicación de control.

### 4. Aplicación de control cliente (estimación de pose de mano)

I. Ejecute la aplicación de la carpeta Firmware/App Control STARPI/starpi_control_app.py con python3.

II. Al iniciar esta comenzara a obtener los datos del acelero-metro recibidos por puerto serie y la estimación de pose determinada mediante la cámara estos datos serán enviados a través de un socket por el protocolo udp a la aplicación de control maestro que se esta ejecutado en el otro dispositivo raspberry pi servidor que controla los movimientos de la prótesis tanto el dispositivo de control de cliente como el servidor maestro deben estar conectados a la misma red.

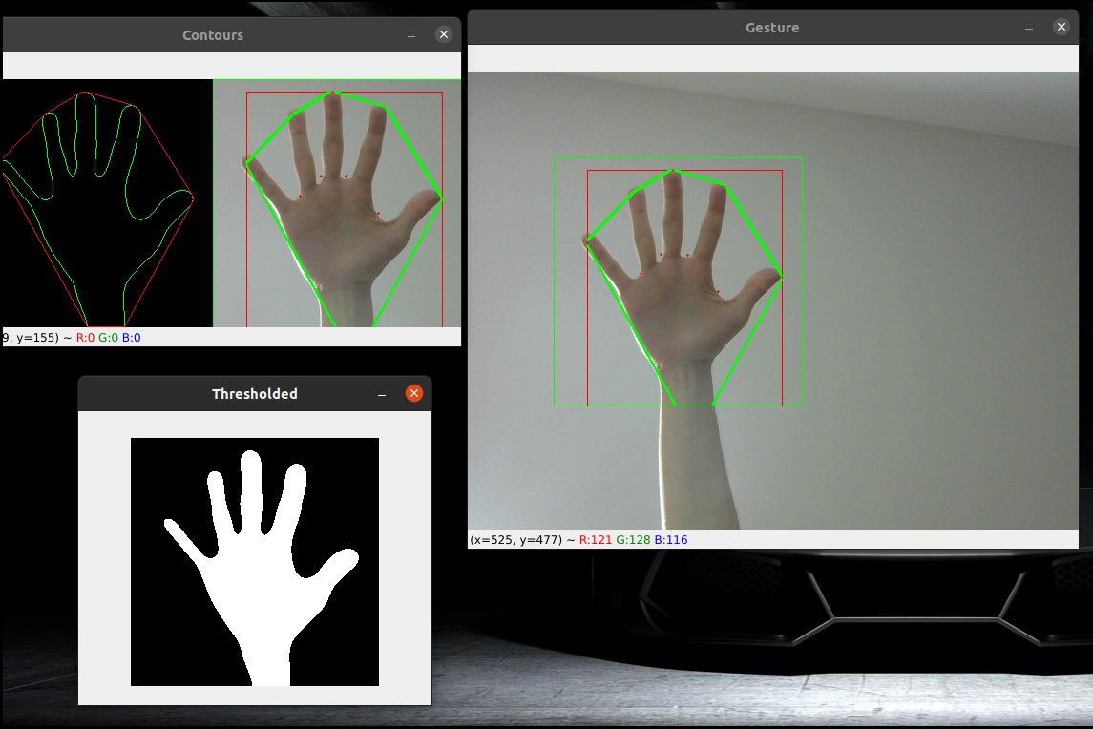
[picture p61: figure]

Interfaces de control gestión de pose de mano

### 5. Visión Remota

I. La visión remota consisten el ver de forma no presencial, inmersiva e interactiva mediante el uso de un visor para teléfonos de realidad virtual y las imágenes captadas a través de una cámara web acoplada junto la prótesis para el control en forma remota permitido la tele-presencia. El teléfono móvil junto con el visor permiten imitar los movimientos de la cabeza para replicarlos en los actuadores acoplado a la cámara creando así un sentido de inmersión.

### 6. App android para el control y adquisición de la imagen de

la visión remota

I. Dentro de la carpeta STARPI/APP encontrara el .apk y el .aia para instalar o editar la app de control de visión remota esta
app | fue | desarrollada | utilizando | appInvetor2
(https://appinventor.mit.edu/) con el archivo .aia podrá editar el código de esta, en la plataforma de appinventor2 en caso de ser necesario.

II. Instale la app en un dispositivo móvil corriendo andorid.

III. Conecte el dispositivo android a la misma red donde están conectados el dispositivo de control de cliente y el servidor maestro.

IV. Al iniciar se encontrara con la siguiente imagen:

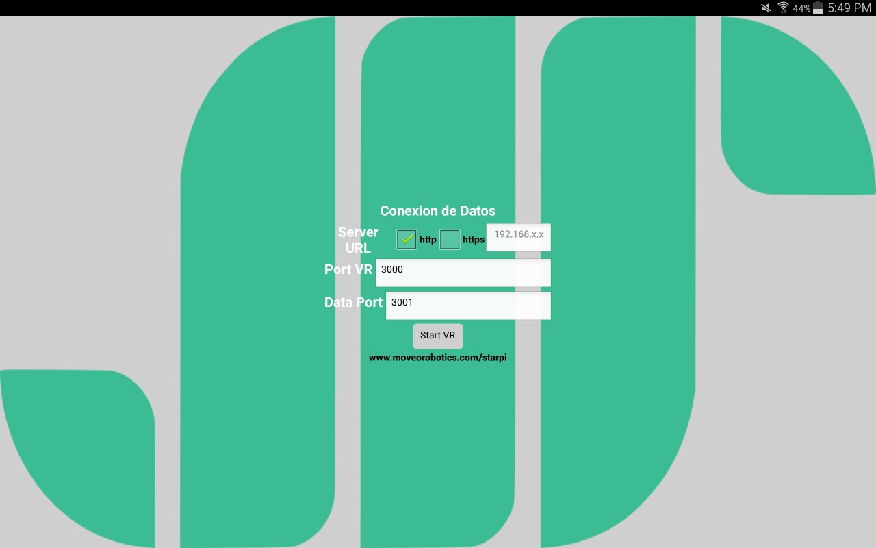
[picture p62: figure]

V. Encontrara 3 recuadros para ingresar la siguiente información: dirección del servidor del control de visión que es la misma del servidor de control maestro de la prótesis, el puerto para visión remota que por defecto es el 3000 y el puerto para el envió de datos del acelero-metro para imitar los movimientos de la cabeza que es el puerto 3001.

VI. Luego de ingresar los datos coloque el el telefoneo sobre una superficie plana y presione el botón “Start VR” la conexión iniciara vera las imagen trasmitidas por la cámara en el formato para usar las gafas de realidad virtual también iniciara la calibración del acelero-metro y el giroscopio, también vera una notificación que menciona que se esta calibrando este proceso tarda al rededor de 3 segundos.

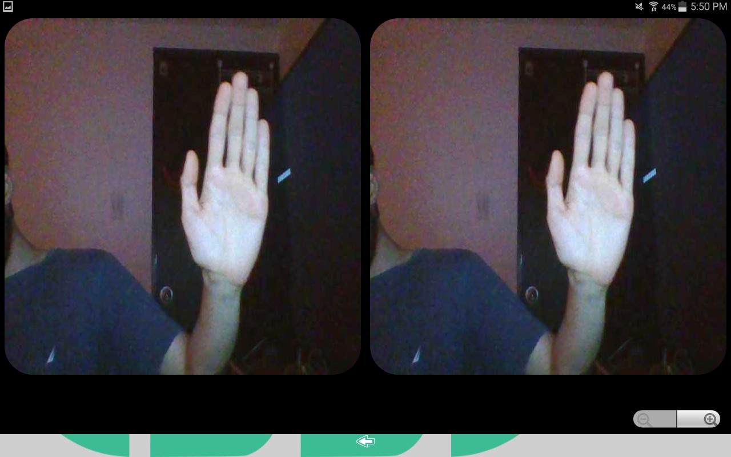
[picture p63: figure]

VII. Cuando la notificación de calibración desaparezca tome el dispositivo y colóquelo en las gafas de realidad virtual, cuando gire su cabeza de izquierda-derecha o de arriba-abajo la cámara imitara esos movimientos dando la sensación de inmersión.

VIII. Si necesita re calibrar el sensor o cambiar la dirección del servidor presione la flecha de color blanco ubicada en el centro de la pantalla en el marco inferir y repita el proceso mencionado anteriormente.

### 7. Para mas información visite nuestro sitio web

www.moveorobotics.com o contáctenos a través de support@moveorobotics.com

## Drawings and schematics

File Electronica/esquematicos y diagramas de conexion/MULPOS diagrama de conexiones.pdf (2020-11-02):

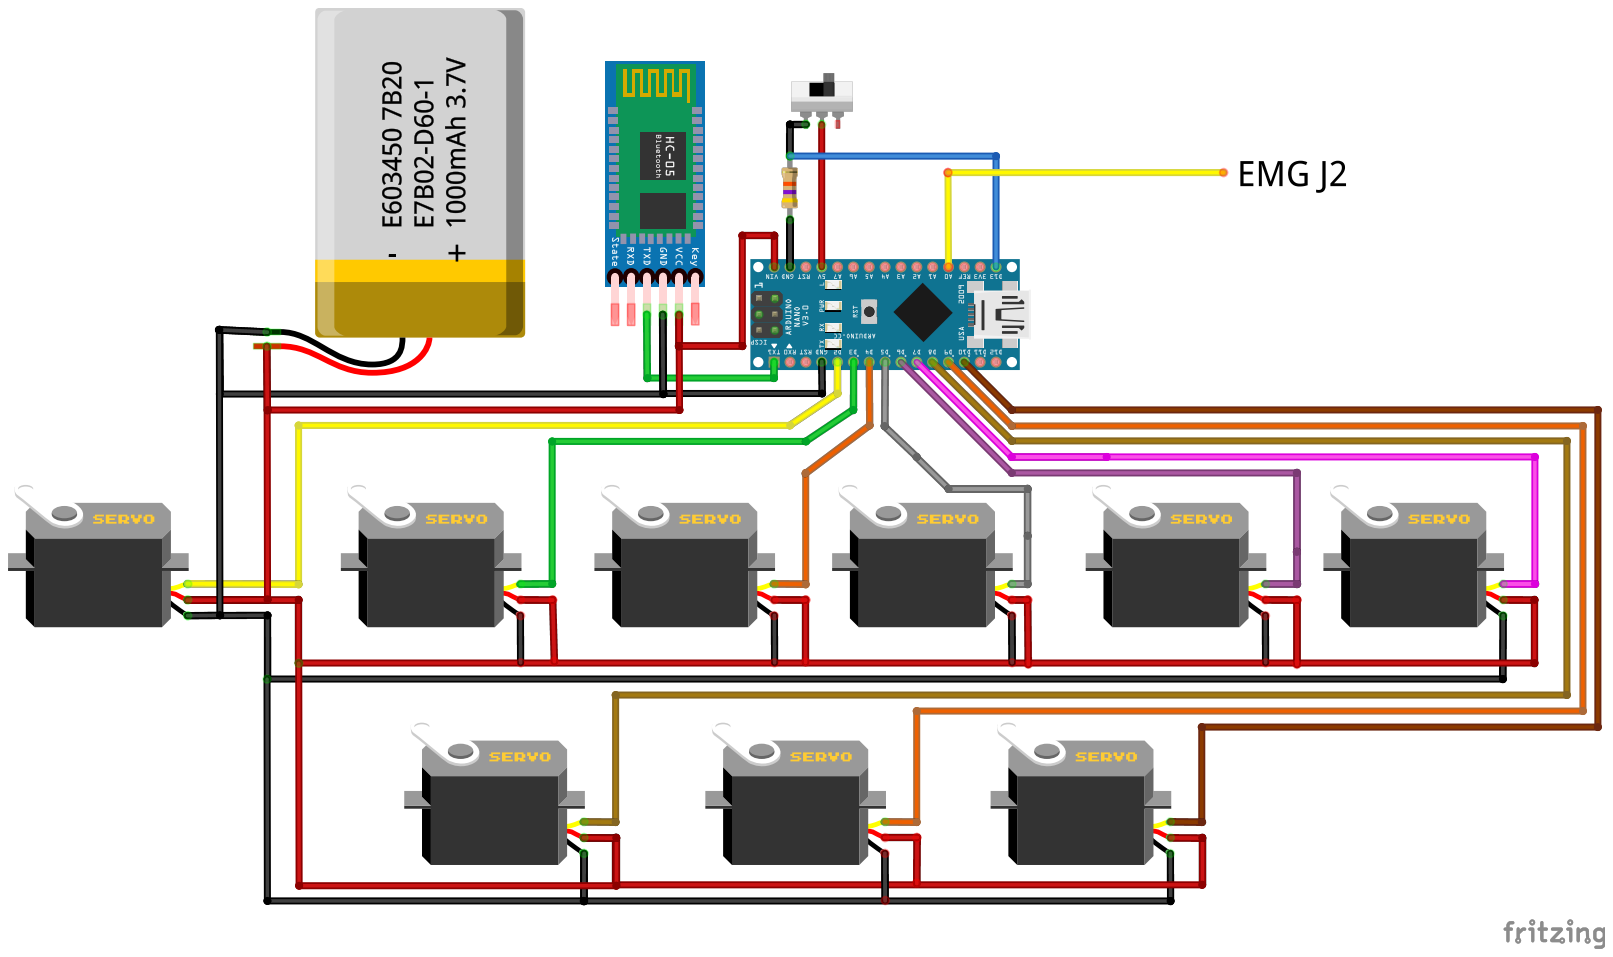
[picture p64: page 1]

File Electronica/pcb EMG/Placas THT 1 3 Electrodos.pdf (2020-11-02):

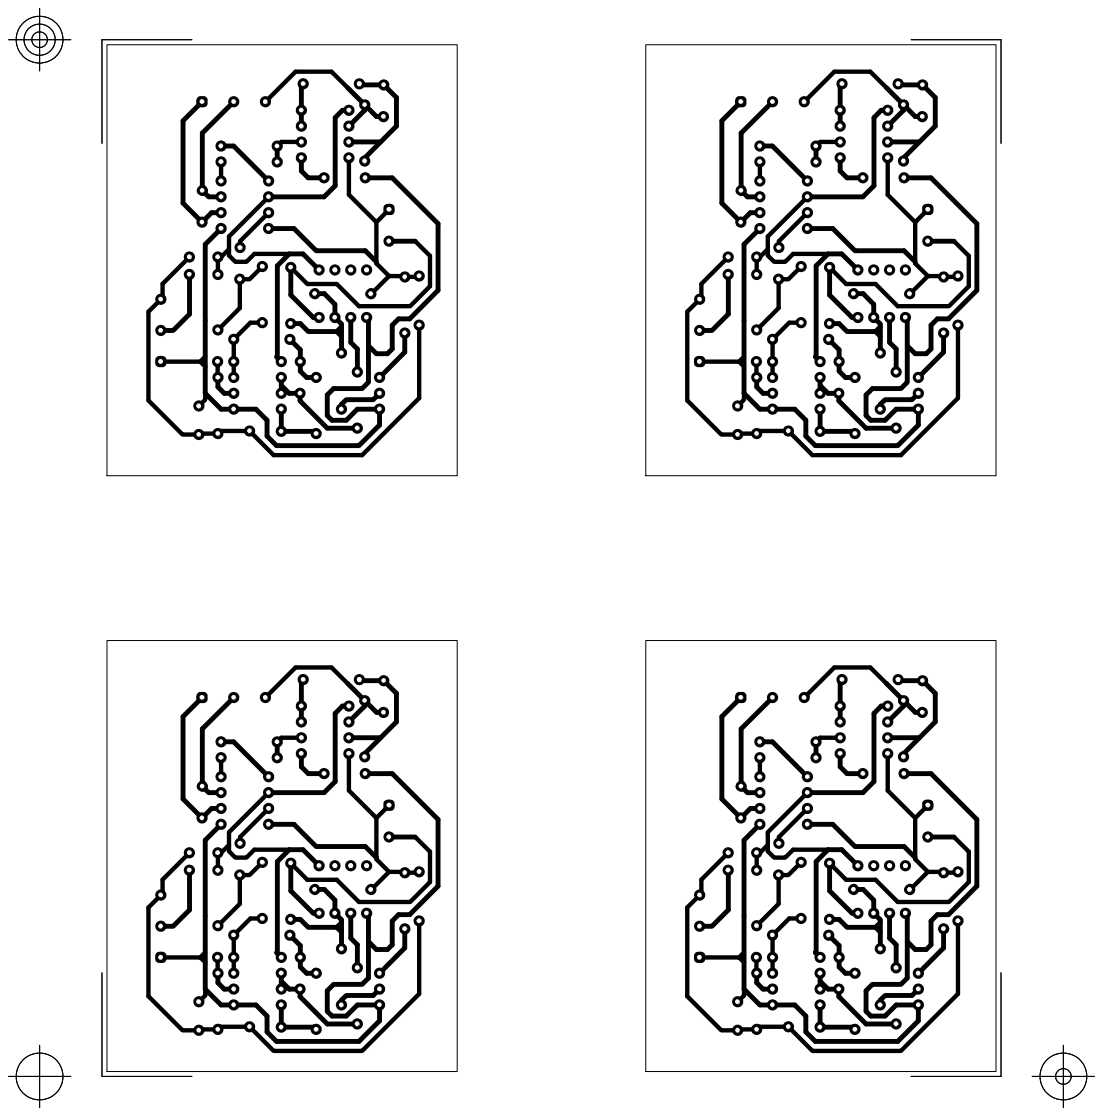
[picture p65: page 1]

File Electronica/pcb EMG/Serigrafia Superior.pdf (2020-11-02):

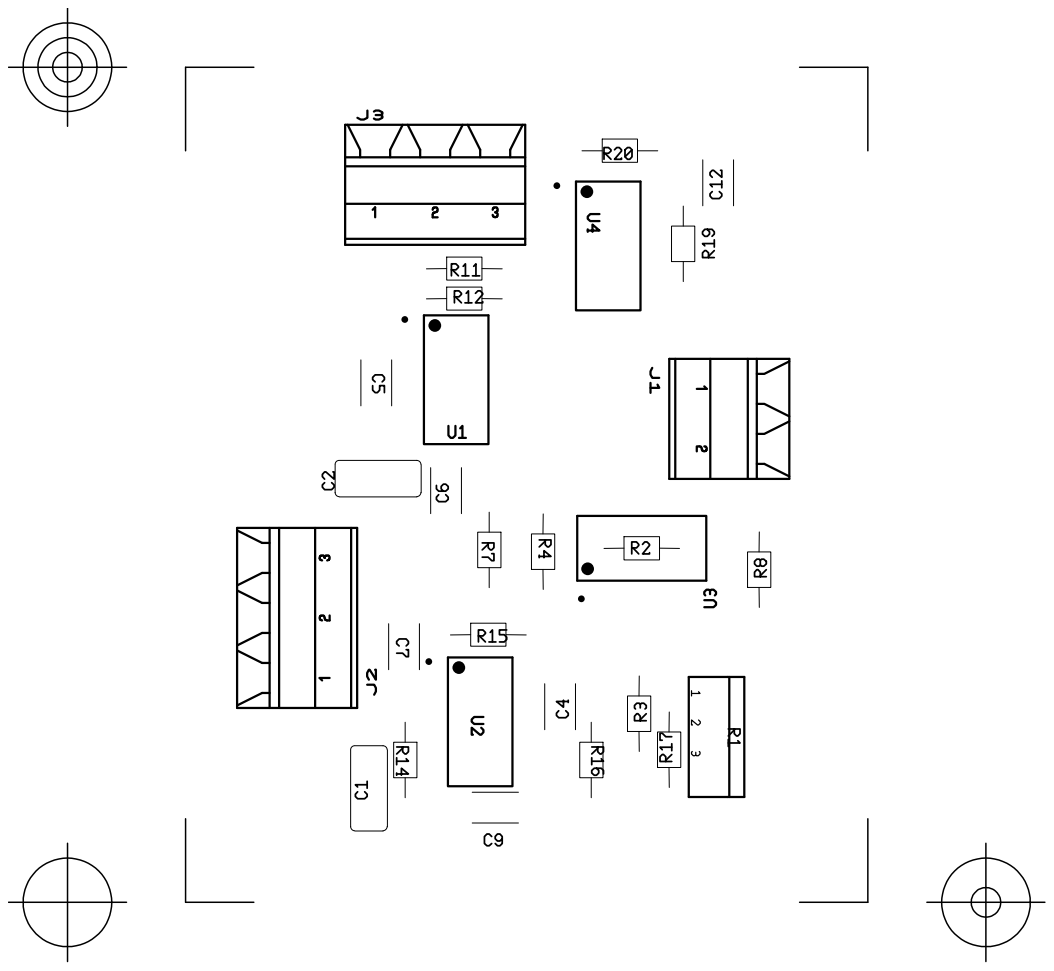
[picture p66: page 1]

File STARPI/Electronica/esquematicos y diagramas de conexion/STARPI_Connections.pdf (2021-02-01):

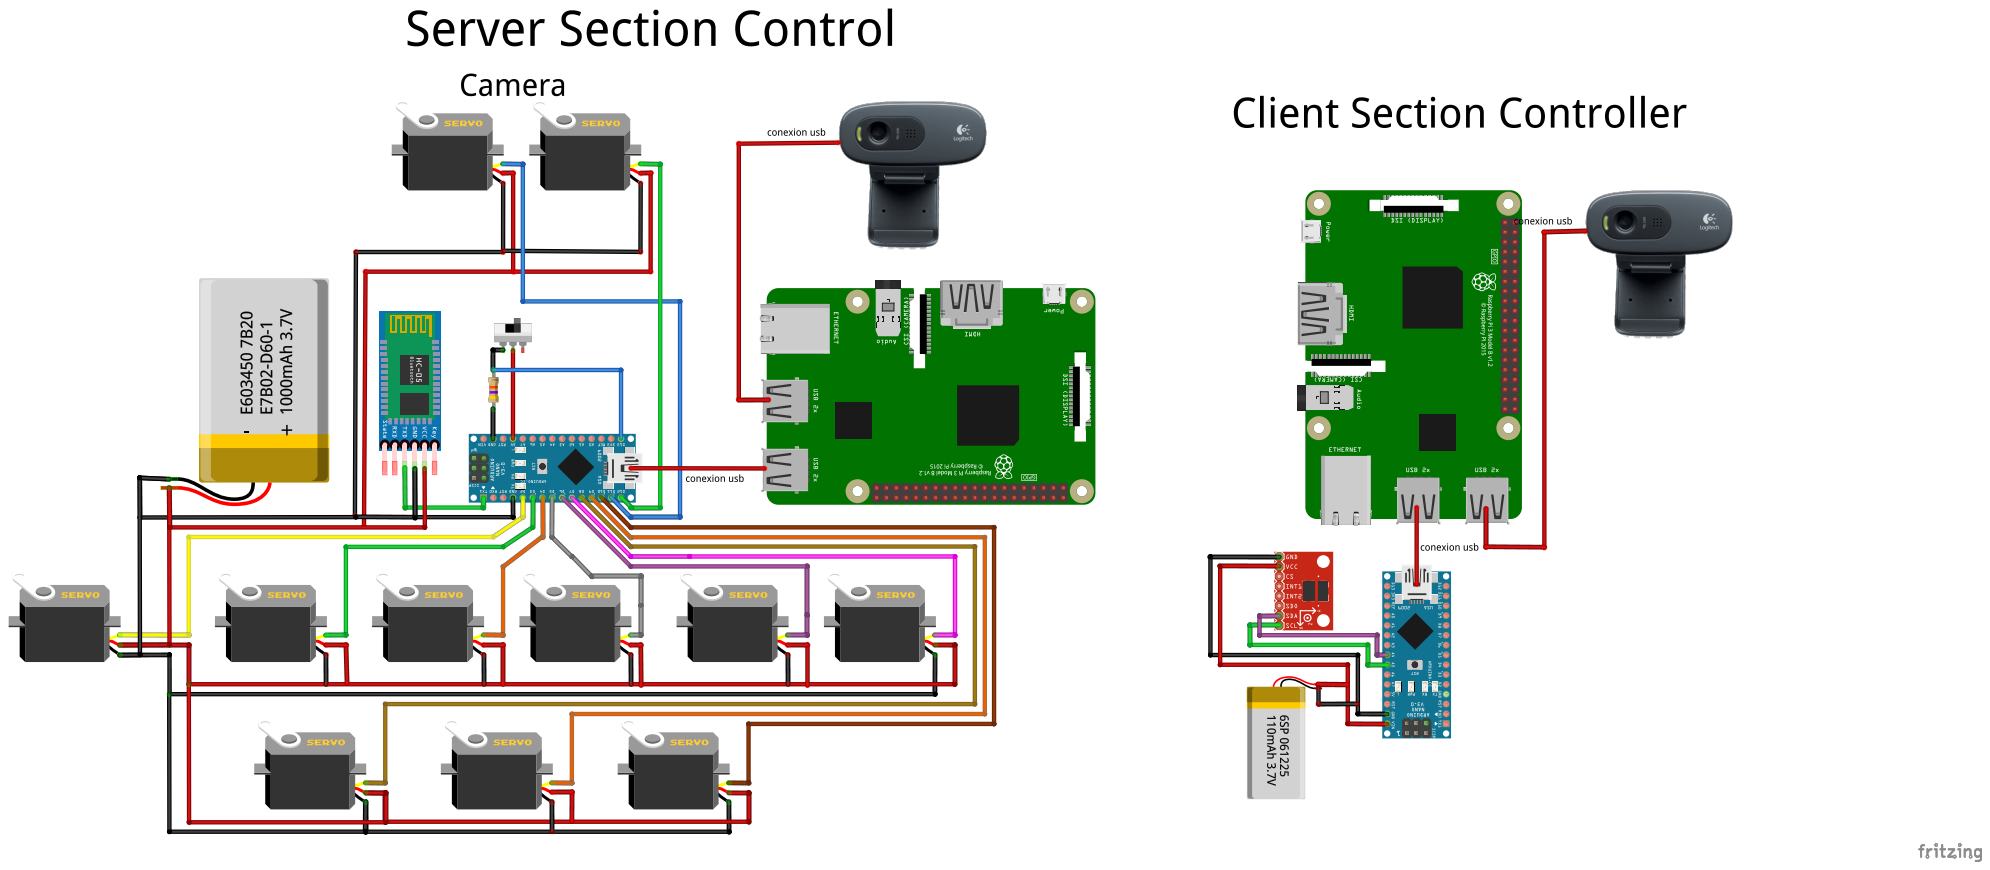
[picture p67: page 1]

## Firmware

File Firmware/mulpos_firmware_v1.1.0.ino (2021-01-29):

/*
 *Codigo de control para el proyecto MULPOS y STARPI, desarrollado y mantenido por Moveo Robotics
 *Para mas informacion y documentacion visita:  https://www.moveorobotics.com o envia un email a support@moveorobotics.com
 *Este poryecto se encuntra protegido bajo licencia MIT
*/

//--------Bibliotecas necesarias-----------//
#include <Servo.h>
//----------------------------------------//

//-------Configuracion de los servos-------//
/*
            Ejes de referencia
                   z
                   |
                   |
                   |_______ y
                  /
                 /
                x
*/

//---------------Muneca y Antebrazo--------//
//Pronacion y Supinacion
Servo servox;
//Flexion y Extencion
Servo servoy;
//Abduccion y Aduccion esta acciones se encuntra desabilitada por el momomento sera integrada en futuras versiones
Servo servoz;
//----------------Dedos-------------------//
//Menique
Servo servof1;
//Anular
Servo servof2;
//Medio
Servo servof3;
//Indice
Servo servof4;
//Pulgar
Servo servof5;
//Opositor de Pulgar
Servo servoPOf5;
//---------Posicion CamaraSTARPI----------//
//YAW
Servo servoCamz;
//PITCH
Servo servoCamy;
//----------------------------------------//

//----------Variables de control----------//
//variables de control para modo app o modo estimacion de pose y/o proyecto STARPI         
int modoAnt = 0;
int valAccion = 0;
int vaPosX = 0;
int vaPosY = 0;
int vjPosX = 0;
int vjPosY = 0;
int vaCamPosZ = 0;
int vaCamPosY = 0;
const int modoCtrl = 13;
//varables de control para modo EMG
String instruccion;  
String comando; 
const int emgPin = A0;  
int emgVal = 0; 
int emgValAnt = 0; 
//asigne aqui el valor maximo obtenido al ejecutar el codigo calibrar emg => "su valor maximo" * 0.7
const int emgLimSup = 1023 * 0.7;
bool flanSub = false; 
bool setTimer = false;  
bool startTimer = false; 
bool seleccionado = false;
int puntero = 0;
int modo = 0;
//aqui puede ajutar el timpo de espera para leer los pulsos musculares
int tiempoEspera = 3000;//tiempo de espera para modo
int tiempoEsperaModo = 2000;//tiempo espera modo en modo
//----------------------------------------//
int tiempoEsperaServos = 180;
int servoPos = 180;
unsigned long antes = 0;  
unsigned long ahora = 0;
unsigned long antesS = 0;  
unsigned long ahoraS = 0;
int varTiempo = 0;
int varTiempoS = 0;
//----------------------------------------//

//-------Configuracion de inicio----------//
void setup()
{ 
  //Configuracion puerto serial
  Serial.begin(38400);
  Serial.setTimeout(5);
  
  //Asignacion de pines para cada servo
  servof1.attach(2);
  servof2.attach(3);
  servof3.attach(4);
  servof4.attach(5);
  servof5.attach(6);
  servoPOf5.attach(7);
  
  servox.attach(8);
  servoy.attach(9);
  servoz.attach(10);
   
  servoCamz.attach(11);
  servoCamy.attach(12);
  
  //Pin para selecionar modo
  pinMode(modoCtrl, INPUT);
  //Verificmaos el modo al iniciar
  modoAnt = digitalRead(modoCtrl);
  
  //Valores de inicio para cada servo posicion inicial
  servox.write(90);
  servoy.write(90);
  servoz.write(90);

  servoCamz.write(90);
  servoCamy.write(90);

  servof1.write(180);
  servof2.write(180);
  servof3.write(180);
  servof4.write(180);
  servof5.write(180);
  delay(1500);
  servoPOf5.write(180);
}
//----------------------------------------//

//----------Bucle principal---------------//
void loop()
{
   modoControl();
}
//----------------------------------------//

//--------Funciones de control------------//

//Define el modo de control
void modoControl()
{
  if(digitalRead(modoCtrl) != modoAnt)
  {
    posServosPredMuneca();
    posServosPredMano();
    posServosPredCam();
    puntero = 0;
    modo = 0;
    servoPos = 180;
    comando = ' ';
    modoAnt = digitalRead(modoCtrl);
  }
  
  if(digitalRead(modoCtrl))
  {
    leerComando();
    epCamAppControlador();
  }
  else
  {
    emgControlador();
  }
  
}

//Lee los comanods que llegan por el puerto serial
void leerComando()
{
   while(Serial.available())
   {
      if(Serial.available()> 0)
      {
        comando = Serial.readStringUntil('|');
      }
      instruccion = comando;
      instruccion.remove(0,1);
      valAccion = instruccion.toInt();
   }
}

//Ejecutar los comandos recibidos para control por app o estmicacio de pose con la camara y/o STRAPI
void epCamAppControlador()
{
  switch(comando[0])
  {
     case 'x':
          //Control de muneca con acelerometro y giroscopio Pronacion y Supinacion
          vaPosX = map(valAccion,-95,95,0,180);
          if (vaPosX >= 75 && vaPosX <= 105)
          {
            servox.write(90); 
          }
          else 
          {
             servox.write(vaPosX);
          }
          break;
    
     case 'y':
          //Control de muneca con acelerometro y giroscopio Flexion y Extencion
          vaPosY = map(valAccion,-90,90,0,180);
          if (vaPosY >= 72 && vaPosY <= 107)
          {
            servoy.write(90); 
          }
          else 
          {
            servoy.write(vaPosY);
          }
          break;

     case 'a':  
          //Control de muneca con joystick pad Pronacion y Supinacion
          vjPosX = constrain(map(valAccion,0,180,180,0),0,180);
          servox.write(vjPosX);
          break;   
      
     case 'b':
          //Control de muneca con joystick pad Flexion y Extencion
          vjPosY = constrain(valAccion,0,180);
          servoy.write(vjPosY);
          break; 

     case 's':
          //Muneca en posicion incial
          servox.write(90);
          servoy.write(90);
          break;

     case '>':
          //Control de camara YAW con acelerometro y giroscopio del telefono con app de vision
          vaCamPosZ = map(constrain(valAccion,-90,90),-90,90,0,180);
          if (vaCamPosZ >= 75 && vaCamPosZ <= 105)
          {
            servoCamz.write(90); 
          }
          else 
          {
            servoCamz.write(vaCamPosZ);
          }
          break;
    
     case '^':
          //Control de camara PITCH con acelerometro y giroscopio del telefono con app de vision
          vaCamPosY = map(valAccion,-90,90,0,180);
          if (vaCamPosY >= 72 && vaCamPosY <= 107)
          {
            servoCamy.write(90); 
          }
          else 
          {
            servoCamy.write(vaCamPosY);
          }
          break;
          
     case 'c': 
           //Cerrar Menique
           servof1.write(0);
           break;
              
     case '1':
           //Abrir Menique 
           servof1.write(180);
           break;
     
     case 'd':
           //Cerrar Anular
           servof2.write(0);
           break;
     
     case '2':
           //Abrir Anular
           servof2.write(180);
           break;
     
     case 'e':
           //Cerrar Medio
           servof3.write(0);
           break;
       
     case '3':
           //Abrir Medio
           servof3.write(180);
           break;
     
     case 'f':
           //Cerrar Indice
           servof4.write(0);
           break;
     
     case '4':
           //Abrir Indice
           servof4.write(180);
           break;
     
     case 'g':
           //Oponer Pulgar y Cerrar
           servoPOf5.write(90);
           delay(1500);
           servof5.write(0);
           break;
           
     case '5':
           //Retonrar Pulagr y Abrir
           servof5.write(180);
           delay(1500);
           servoPOf5.write(180);
           break;
          
     case 'h':
           //Sujetar
           servof1.write(0);
           servof2.write(0);
           servof3.write(0);
           servof4.write(0);
           servoPOf5.write(90);
           delay(1500);
           servof5.write(0);
           break; 
     case '6':
           //Soltar
           servof1.write(180);
           servof2.write(180);
           servof3.write(180);
           servof4.write(180);
           servof5.write(180);
           delay(1500);
           servoPOf5.write(180); 
           break;  
      
     case 'j':
           //Saludar
           servoy.write(10);
           servox.write(150);
           delay(700);
           servox.write(30);
           delay(700);
           servox.write(150);
           delay(700);
           servox.write(30);
           delay(700);
           servox.write(150);
           delay(700);
           comando = 'm' ;   
           break;
         
     case 'k':
           //Despedirse
           servoy.write(90);
           servox.write(180);
           servof1.write(5);
           servof2.write(180);
           servof3.write(5);
           servof4.write(180);
           servof5.write(5);
           delay(5000);
           comando = 'm' ;
            break;
           
     case 'm':
           //Posicion Inicial
           servox.write(90);
           servoy.write(90);
           servof1.write(180);
           servof2.write(180);
           servof3.write(180);
           servof4.write(180);
           servof5.write(180);
           delay(1500);
           servoPOf5.write(180);
           comando = ' ';
           break;
           
     case 'o':
           //Giro a la Derecha
           servox.write(180);
           break;
           
     case 'p':
           //Giro a la Izquierda
           servox.write(0);
           break;
           
     case 'q':
           //Felxion hacia Arriba
           servoy.write(10);
           break;
           
     case 'n':
           //Flexion hacia Abajo
           servoy.write(180);
           break;
           
     case 'l':
           //Posicion inicial Muneca
           servox.write(90);
           servoy.write(90);
           break;
           
     case 'r':
           //Senalar con el Indice "ahi"
           servox.write(90);
           servoy.write(90);
           servof1.write(0);
           servof2.write(0);
           servof3.write(0);
           servof4.write(180);
           servoPOf5.write(90);
           delay(1500);
           servof5.write(0);
           delay(5000);
           comando = 'm' ;
           break;
           
     case 't':
           //Gesto de Pulgar Abajo "mal"
           servoy.write(90);
           servox.write(0);
           servof1.write(0);
           servof2.write(0);
           servof3.write(0);
           servof4.write(0);
           servoPOf5.write(180);
           servof5.write(180);
           delay(5000);
           comando = 'm' ;
           break;
           
     case 'u':
           //Sujetar con cierre medio
           servox.write(90);
           servoy.write(90);
           servof1.write(90);
           servof2.write(90);
           servof3.write(90);
           servof4.write(90);
           servoPOf5.write(90);
           delay(1500);
           servof5.write(90);
           break; 
           
     case 'v':
           //Sujecion con dedos modo pinza
           servox.write(90);
           servoy.write(90);
           servof1.write(0);
           servof2.write(0);
           servof3.write(0);
           servof4.write(180);
           servof5.write(180);
           delay(3000);
           servoPOf5.write(90);
           delay(1500);
           servof5.write(0);
           servof4.write(0);
           break;
           
     case 'z':
           //Senal con el dedo Medio "fuck you"
           servox.write(90);
           servoy.write(90);
           servof1.write(0);
           servof2.write(0);
           servof3.write(180);
           servof4.write(0);
           servoPOf5.write(90);
           delay(1500);
           servof5.write(0);
           delay(5000);
           comando='m' ;
           break;
//----------------------------------------//          
//-------Comandos Estimacion de Pose-------//                     

     case '!':
           //Sujetar, cerrar todos los dedos
           servoPOf5.write(90);
           delay(1500);
           servof1.write(0);
           servof2.write(0);
           servof3.write(0);
           servof4.write(0);
           servof5.write(0);
           break;
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
